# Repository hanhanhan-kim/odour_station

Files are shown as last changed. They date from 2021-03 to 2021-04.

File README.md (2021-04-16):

# Odour station

Hardware for delivering odours. Can be modified so that the second manifold controls for odour source direction, instead of providing additional odour types. Will Dickson designed the PCB for controlling the solenoid valves. Will Dickson wrote the [original firmware and software](https://github.com/willdickson/switchx7), which I [slightly modified](https://github.com/hanhanhan-kim/switchx7) so that valve command signals can be copied to the expansion port and streamed to an acquisition device, such as a DAQ. 

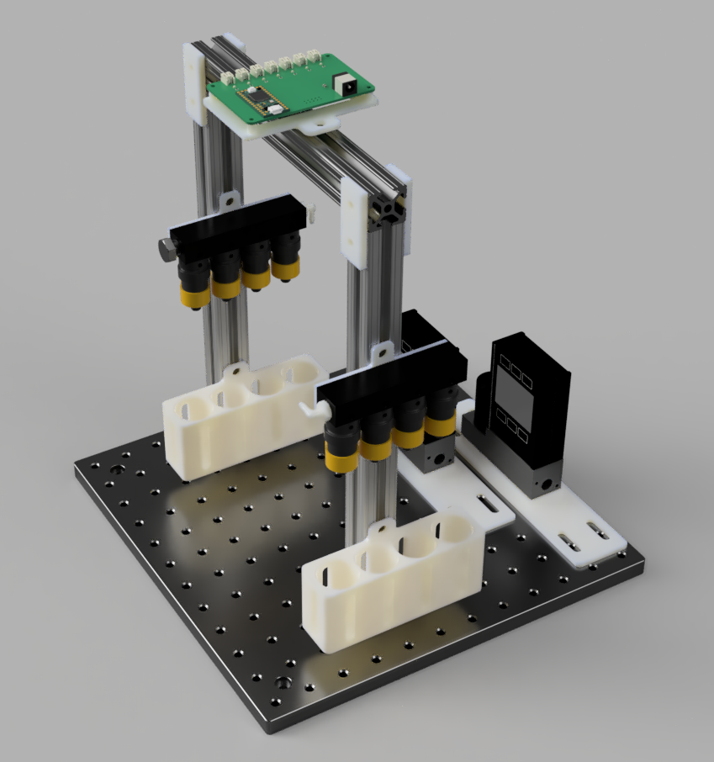
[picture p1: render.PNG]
render


## Hardware

### BOM 

In addition to standard electronics equipment and access to a 3D-printer:

| Item                                                         | Price (USD) | Quantity        | Source                                                       |
| ------------------------------------------------------------ | ----------- | --------------- | ------------------------------------------------------------ |
| Valves*                                                      | 32.13       | 2 or more       | Clippard<br />[EVO-3M-24-L](https://www.clippard.com/part/EVO-3M-24-L) |
| Manifold **                                                  | 17.14       | 1 or more       | Clippard<br />[15481-4]()                                    |
| Barb fittings for valves                                     | 10.61 / 10  | 1 or more packs | Clippard<br />[11752-1-ENP-PKG](https://www.clippard.com/part/11752-1-ENP-PKG) |
| Headless screw plug                                          | 8.93 / 10   | 1 or more packs | Clippard <br />[0035-2-PKG](https://www.clippard.com/part/0035-2-PKG) |
| Plug with external hex drive                                 | 1.06        | 1 or more       | McMaster-Carr<br />[4515K208](https://www.mcmaster.com/4515K208/) |
| Barbed elbow fitting                                         | 7.68 / 1    | 1 pack          | McMaster-Carr<br />5121K631                                  |
| End-feed single nuts with button heads for t-slotted framing | 1.85 / 4    | 3 or more packs | McMaster-Carr<br />[47065T139](https://www.mcmaster.com/47065T139/) |
| 80-20 beams***                                               | 5.84        | 3               | McMaster-Carr<br />[47065T101](https://www.mcmaster.com/47065T101-47065T411/) |
| Silver gusset bracket for 80-20 beams                        | 6.54        | 2 or more       | McMaster-Carr<br />[47065T663](https://www.mcmaster.com/47065T663/) |
| Breadboard                                                   | 155.53      | 1               | Thor Labs<br />[MB12](https://www.thorlabs.com/thorproduct.cfm?partnumber=MB12) |
| Mass Flow Controller                                         | 1161.00     | 1               | Alicat<br />MC-5SLPM-D<br />5M, RIN, 5IN, Gas: Air           |
| Mass Flow Controller                                         | 1161.00     | 1               | Alicat<br />MC-500SCCM-D<br />5M, 5IN, GAS: Air              |

\* These valves can be fully ported, and so can be used as either 3-way or 2-way valves. I didn't quite figure out how to use them as 3-way diverting valves, so I've been using them as regular 2-way valves. 

** Or some other Clippard manifold that's compatible with Clippard's EV valves. 

*** Or whatever desired length.

Additional components for connecting and routing the tubing are necessary. The inlet and outlet of the mass flow controllers have 1/8 NPT threads. Upstream of the valves, I tend to use 1/8" ID tubing, and upstream of the mass flow controllers, I tend to use high-pressure-rated 1/4" ID tubing. Here are some parts I found generally useful for controlling fluid movements:

| Item                                                      | Price (USD) | Notes                                                        | Source                                                       |
| --------------------------------------------------------- | ----------- | ------------------------------------------------------------ | ------------------------------------------------------------ |
| Barbed inline filter for 1/4" tube ID                     | 6.25        | To filter particulates downstream of the breathing air's charcoal filter. | McMaster-Carr<br />[8991T32](https://www.mcmaster.com/8991T32/) |
| High-pressure soft PVC tubing                             | 0.73 / ft   | To route air supply prior to the mass flow controllers' regulating functions. | McMaster-Carr<br />[52375K12](https://www.mcmaster.com/52375K12/) |
| Barbed fitting for 1/8" tube ID x 1/8 NPT male            | 5.31 / 10   | To connect to mass flow controller's output  end.            | McMaster-Carr<br />[5121K371](https://www.mcmaster.com/5121K371/) |
| Barbed fitting for 1/4" tube ID x 1/8 NPT male            | 5.58 / 10   | To connect to mass flow controller's input end.              | McMaster-Carr<br />[5121K391](https://www.mcmaster.com/5121K391/) |
| Barbed fitting for 1/4" tube ID, wye connector            | 18.01 / 10  | To split the breathing air into the odour input mass flow controller and the carrier stream mass flow controller. | McMaster-Carr<br />[5463K723](https://www.mcmaster.com/5463K723-2974K284/) |
| 90 degree barbed fitting elbow connector for 1/8" tube ID | 5.79 / 10   | To better route the tubing downstream of the mass flow controllers. | McMaster-Carr<br />[5121K903](https://www.mcmaster.com/5121K903/) |
| Luer lock socket and barb for 1/8" ID                     | 4.36 / 10   | To add modularity to the components.                         | McMaster-Carr<br />[51525K213](https://www.mcmaster.com/51525K213/) |
| Luer lock plug and barb for 1/8" ID                       | 3.87 / 10   | To add modularity to the components.                         | McMaster-Carr<br />[51525K123](https://www.mcmaster.com/51525K123/) |
| Luer lock socket and barb for 1/4" ID                     | 4.25 / 10   | To add modularity to the components.                         | McMaster-Carr<br />[51525K216](https://www.mcmaster.com/51525K216/) |
| Luer lock plug and barb for 1/4" ID                       | 4.89 / 10   | To add modularity to the components.                         | McMaster-Carr<br />[51525K126](https://www.mcmaster.com/51525K126/) |

### Hook-up

The hook-up is straightforward. To connect the solenoid valves to the PCB, crimp the JST-PH terminals onto the leads of the valves. The valves do not possess polarity. Alternatively, if crimping the terminals is too cumbersome, simply splice [these pre-crimped JST-PH wires](https://www.sparkfun.com/products/8671) onto the solenoid leads. See the solenoid controller’s [documentation](https://github.com/willdickson/teensy3x_solenoid_driver) for remaining details. 

### Assembly

Print all 3D-printed components. Screw everything together—parts are generally assembled with 1/4"-20 screws or 8-32 screws, except for the mass flow controllers, which are mounted onto their adaptors via 8-32 screws. Parts for fluid management use 10-32-threads or 1/8"-NPT threads. Route the tubing as necessary. Use an activated charcoal filter upstream of both mass flow controllers, and then place an in-line particle filter downstream of the charcoal filter.

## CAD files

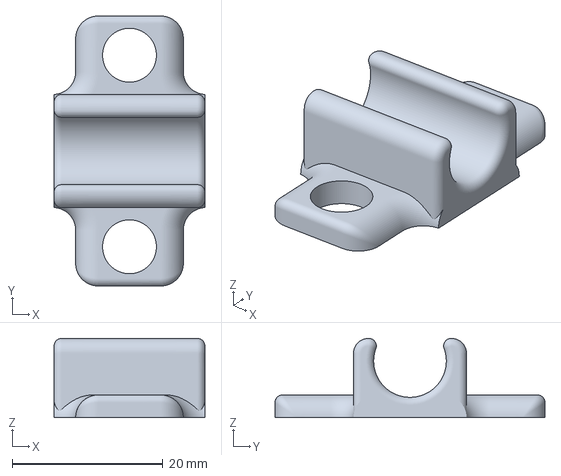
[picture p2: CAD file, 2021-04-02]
3mfs/ptfe_tube_holder.3mf
20.0 x 35.8 x 10.5 mm

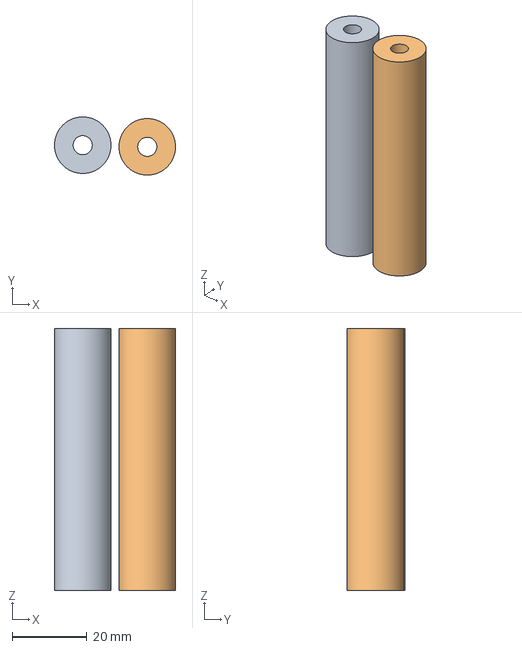
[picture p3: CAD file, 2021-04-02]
3mfs/quarter_20_riser.3mf
32.3 x 15.5 x 70.0 mm
quarter_20_riser.stl x 2

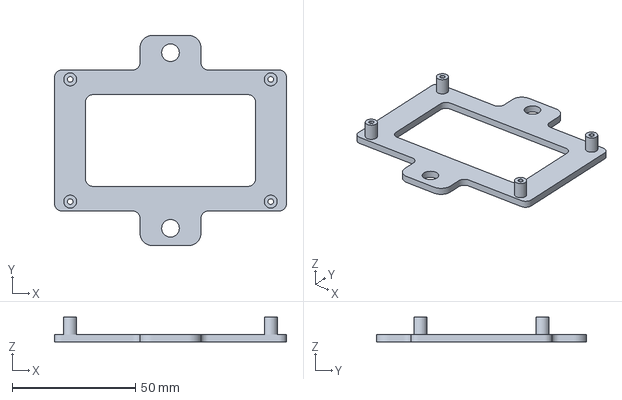
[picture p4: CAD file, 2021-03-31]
3mfs/PCB_platform.3mf
94.0 x 85.2 x 10.0 mm

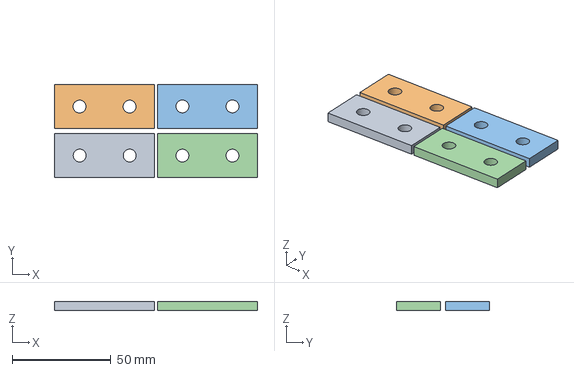
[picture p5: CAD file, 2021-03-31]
3mfs/joining_plates.3mf
103.0 x 47.2 x 4.76 mm
joining_plates.stl x 4

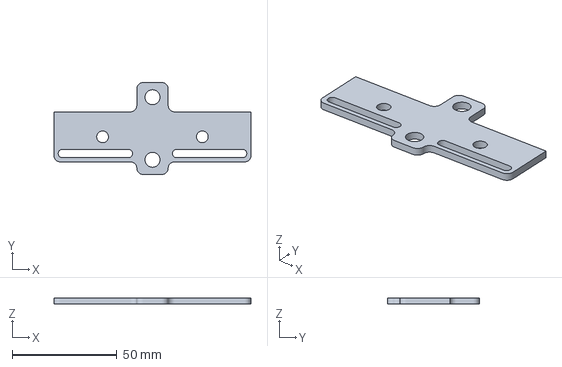
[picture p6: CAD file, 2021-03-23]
3mfs/manifold_holder.3mf
94.0 x 43.9 x 3.00 mm

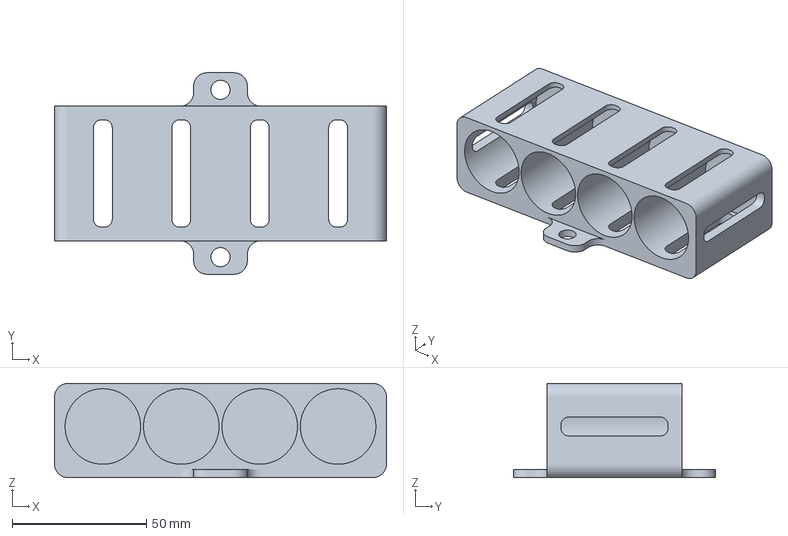
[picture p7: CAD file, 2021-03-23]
3mfs/vial_holder.3mf
123.5 x 75.0 x 35.0 mm

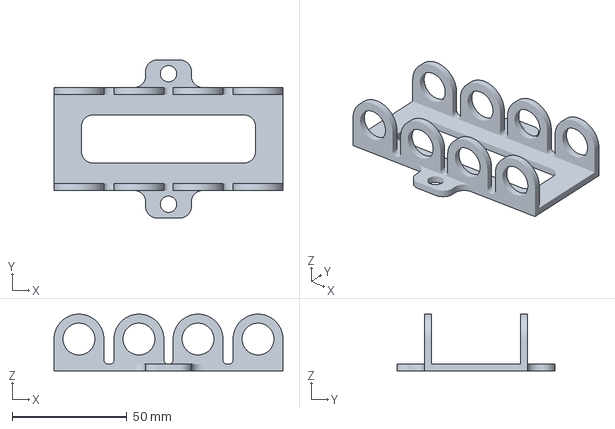
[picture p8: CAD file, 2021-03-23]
3mfs/syringe_holder.3mf
100.0 x 69.0 x 24.8 mm

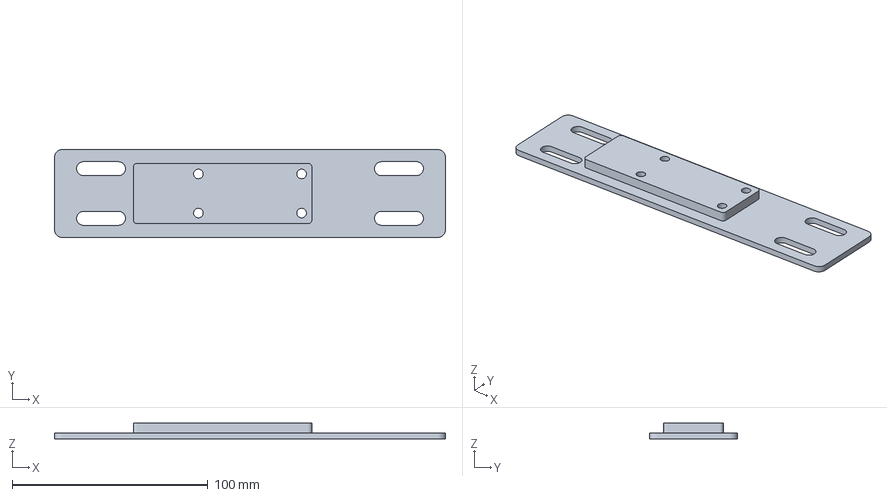
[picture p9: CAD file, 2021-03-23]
3mfs/alicat_mass_flow_controller_to_bboard.3mf
200.0 x 45.0 x 8.18 mm

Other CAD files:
stls/PCB_platform.stl
stls/alicat_mass_flow_controller_to_bboard.stl
stls/joining_plates.stl
stls/manifold_holder.stl
stls/ptfe_tube_holder.stl
stls/quarter_20_riser.stl
stls/syringe_holder.stl
stls/vial_holder.stl

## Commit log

2021-03-23 add stls and 3mfs
    [PCB_platform.3mf, PCB_platform.stl, alicat_mass_flow_controller_to_bboard.3mf, alicat_mass_flow_controller_to_bboard.stl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]
2021-03-31 add joining plates and mounts to PCB platform
    [PCB_platform.3mf, PCB_platform.stl, joining_plates.3mf, joining_plates.stl]
2021-04-01 add holder for thicker PTFE tubing
    [ptfe_tube_holder.3mf, ptfe_tube_holder.stl]
2021-04-02 add teflon holder parts
    [ptfe_tube_holder.3mf, ptfe_tube_holder.stl, quarter_20_riser.3mf, quarter_20_riser.stl]
